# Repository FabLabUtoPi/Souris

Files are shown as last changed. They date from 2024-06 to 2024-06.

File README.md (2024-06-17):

Souris - Projet Souris - Lauréat ANCT  
[Voir le projet sur La Base](https://lesbases.anct.gouv.fr/ressources/souris-adaptee-pour-personne-en-situation-de-handicap-laureat-ami-outiller-la-mediation-numerique)   
# Une souris adaptée pour personnes en situation de handicap
souris_AMI
## A l’origine du projet 
Un ami aveugle de naissance réalise des podcasts. Il se plaint de l’utilisation d’une souris « classique » car parfois lorsqu’il pense déplacer la souris horizontalement pour sélectionner un mot, il la déplace en diagonale et sélectionne plusieurs mots, plusieurs lignes. Il existe des souris adaptée mais leur prix est hors de sa portée car les aides ne couvrent pas la dépense à engager.
Le projet d’une souris adaptée est proposé au FabLab et accepté.
## L’approche du FabLab UtoPi
### Cahier des charges
#### Généralités
Au sein du **FabLab UtoPi** se crée une équipe qui va se consacrer au développement de la souris adaptée. Au vu des prix pratiqués pour ce genre de matériel (~700 à 800€), le premier élément pris en compte est le coût. Il est décidé de limiter le coût de la souris aux alentours de 50€ maxi pour la mettre à la portée d’un maximum de personnes.

#### Choix du microcontrôleur
Au sein du **FabLab UtoPi** plusieurs possibilités de développement existent. Les microcontrôleurs utilisés sont le STM32, la famille des PIC, Arduino et Raspberry Pi PICO. 
En raison des possibilités de programmation en MicroPython du Raspberry Pi PICO, ce qui le rend accessible à un plus large nombre d’utilisateurs (le langage Python est le langage choisi par l’Éducation Nationale pour les lycées), c’est ce modèle qui a été choisi. Son prix autour de 5€ permet de conserver un prix raisonnable pour les souris produites.

#### Déplacement du curseur

Pour limiter les déplacements aux directions HAUT, BAS, DROITE et GAUCHE, le choix s’est porté sur un joystick. Celui-ci permet de plus une adaptation en cas de problème de préhension. Les tests avec un joystick analogique (avec des potentiomètres) et un numérique (avec des switch) ont abouti au choix de la version numérique.
Si l’utilisateur déplace le joystick en diagonale (volontairement ou par inadvertance), il sera averti par un vibreur intégré à la souris, qui fournit un retour haptique.

#### Boutons additionnels
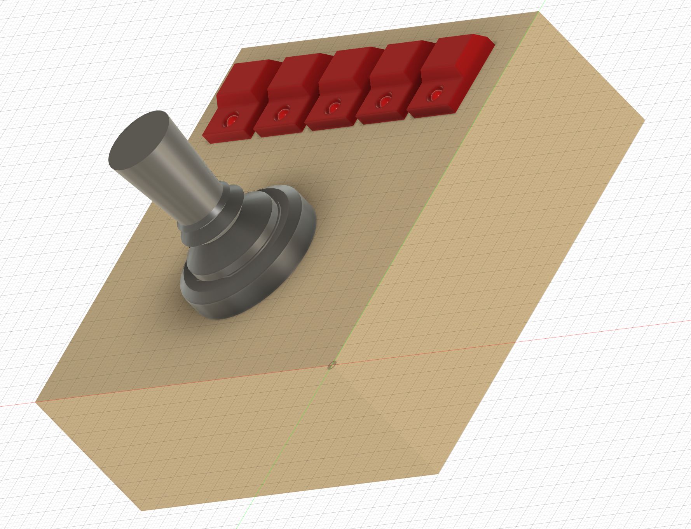
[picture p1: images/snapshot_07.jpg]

Lorsque le joystick sera maintenu en position un certain temps (programmable), le curseur sur l’écran se déplacera automatiquement dans la direction choisie. 
Boutons additionnels
La souris sera dotée de 5 boutons placés devant le joystick. Selon les retours d’expérience, ce nombre pourra être modifié ainsi que les emplacements. Les fonctions retenues pour ces boutons sont : Clic gauche, clic droit, appel d’un logiciel (programmable, par défaut NVDA), roulette UP, roulette DOWN.

#### Le retour haptique
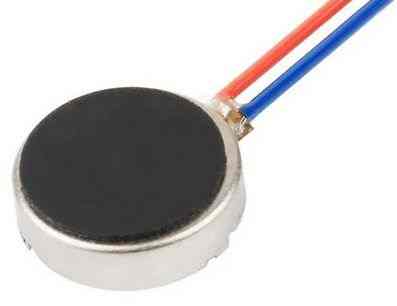
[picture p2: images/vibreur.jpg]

Pour assurer un retour haptique (tactile), la souris sera munie d’un vibreur. C’est un moteur miniature qui entraîne une masselotte excentrée et produit des vibrations. Ce genre de vibreur équipe les tablettes et les smartphones. Le vibreur pourra signaler des actions comme le déplacement en diagonale, confirmer l’activation d’une touche…
Une action lors de la connexion de la souris (appui sur touche ou combinaison de touches) permettra de dévalider l’utilisation du retour haptique.

#### Retour auditif
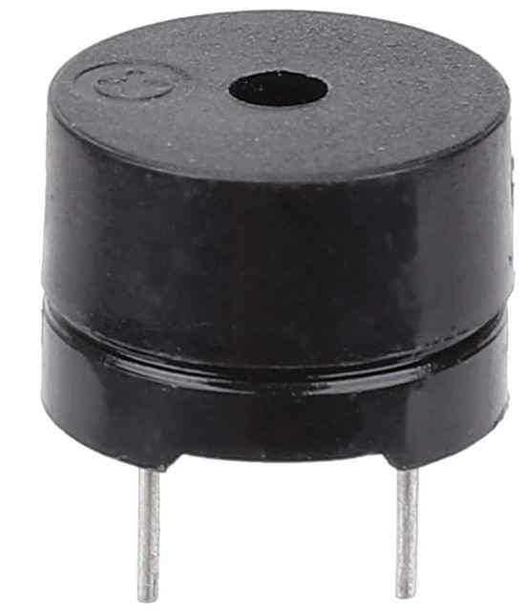
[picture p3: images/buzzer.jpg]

Un retour auditif (sous forme de clic ou de bip) est envisagé avec la présence d’un buzzer activé par une des sorties du Raspberry Pi PICO. 
Une action lors de la connexion de la souris (appui sur touche ou combinaison de touches) permettra de dévalider l’utilisation du retour auditif.  

#### Sortie du programme
La programmation du Raspberry Pi PICO se fait via la connexion USB. Une combinaison touche/joystick sera prévue pour arrêter le programme et donner accès au microcontrôleur pour pouvoir modifier le programme.
Combinaison prévue : Touche centrale + touche la plus à droite + joystick en BAS. Si cette combinaison est activée en cours de programme, le programme allume les LEDs des 5 touches, envoie sur le port console un message d’avertissement, puis s’arrête. Cela permet au développeur de reprendre la main pour apporter plus facilement des modifications. Sur les modèles définitifs cette fonction pourra être dévalidé.  

## Réalisation technique
### Brochage du Raspberry Pi PICO
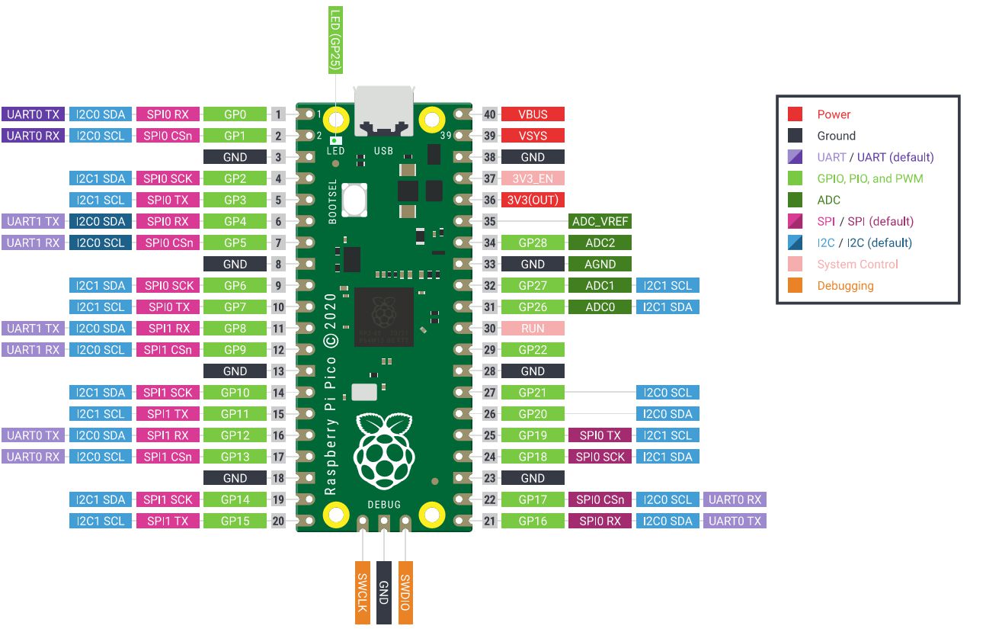
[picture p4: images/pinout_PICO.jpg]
  
Le Raspberry Pi PICO expose ses Entrées/Sorties GPIO comme ci-dessus. Le choix a été fait d’utiliser la partie gauche de la carte pour connecter les différents matériels utilisés (switch, LEDs, vibreur et buzzer). Les bornes de masse (GND) intercalées permettent de connecter la masse aux endroits souhaités.
La partie droite comporte une dizaine de GPIO supplémentaires, dont des possibilités d’Entrée Analogique qui pourront éventuellement être utilisées pour des développements futurs.\\\

### Schéma global de la souris adaptée
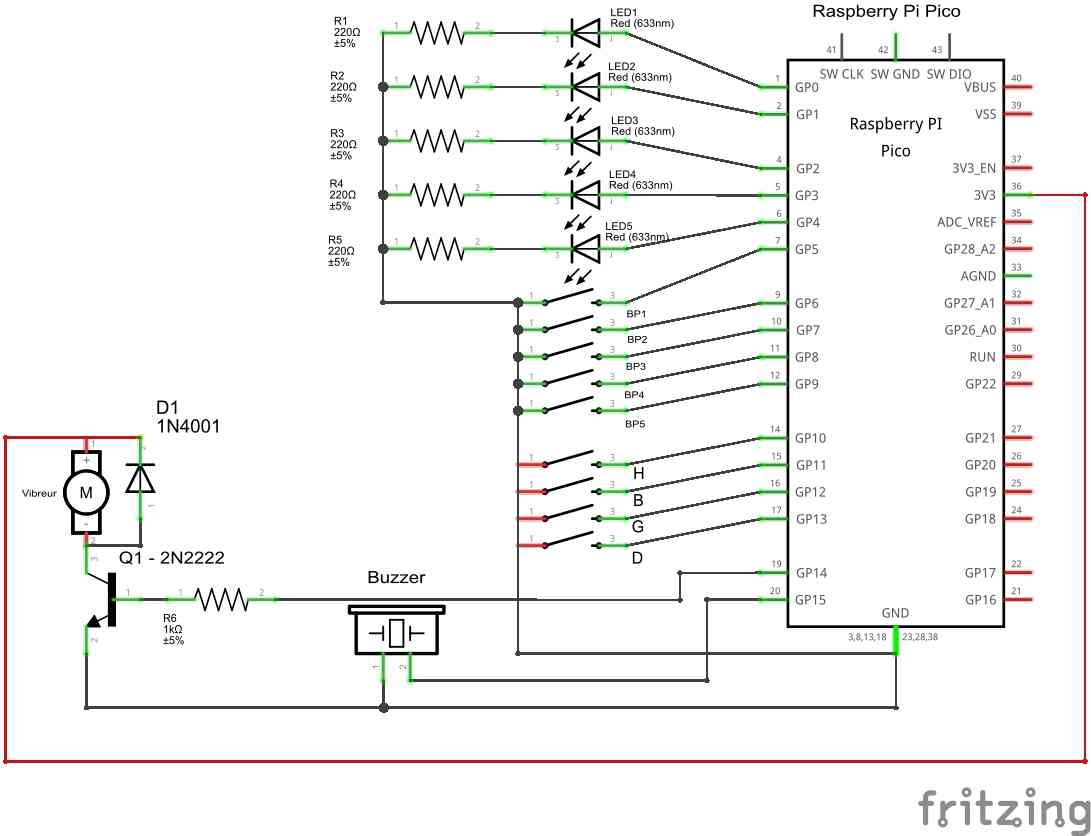
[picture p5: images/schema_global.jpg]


Le schéma montre la connexion des LEDs (GP0 à GP4), des 5 boutons poussoirs (GP5 à GP9) et du joystick (GP10 à GP13). 
Le vibreur est connecté à la sortie GP14, et le buzzer à la sortie GP15.
La sortie GP15 active le vibreur. La diode anti retour aux bornes du moteur est nécessaire avec le moteur utilisé.

### Plaque support des boutons poussoirs
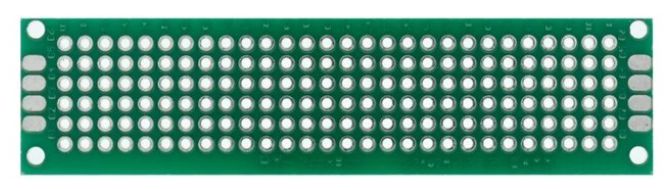
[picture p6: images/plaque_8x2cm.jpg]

La plaque support des boutons poussoirs choisie est un modèle de carte prototype double face universel. Pour la version définitive on pourra envisager la fabrication d’un PCB (circuit imprimé) sur mesure et plus adapté. Mais pour le prototype, cette solution était la plus rapidement mise en œuvre.

### Câblage des Boutons poussoirs
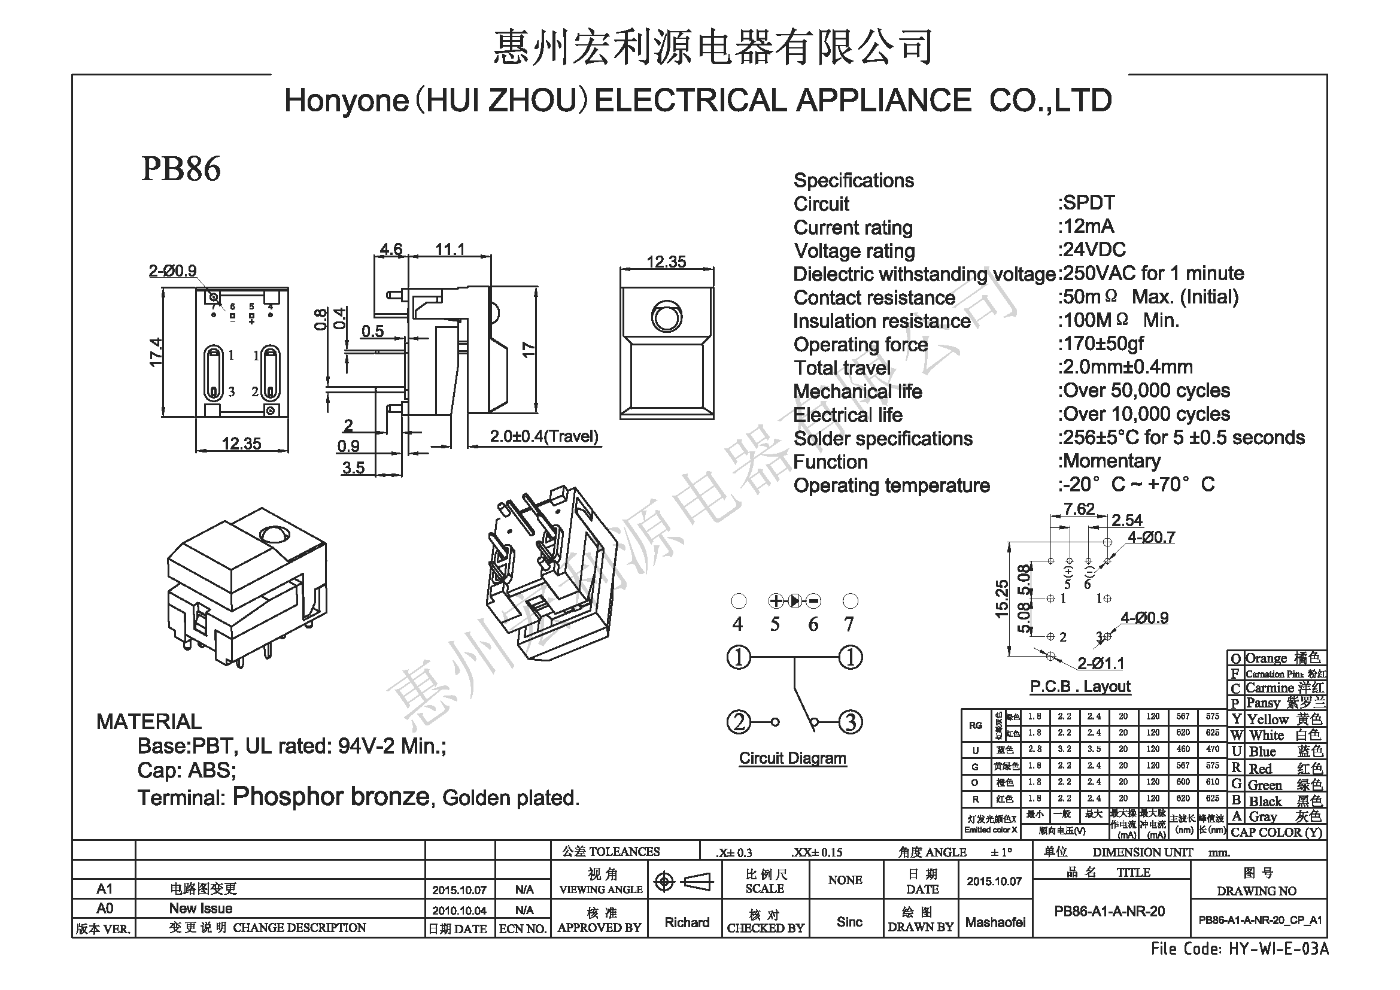
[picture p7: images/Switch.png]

Les boutons poussoirs sont documentés ci-dessus. En position repos, les broches 1 et 3 sont reliées (position NF = Normalement Fermé). Quand on appuie sur le bouton poussoir 1-3 s’ouvre et 1-2 se ferme (NO = Normalement ouvert).
La LED est connectée aux bornes 5 (anode) et 6 (cathode). Il conviendra d’ajouter une résistance en  série avec la LED pour protéger la sortie du Raspberry Pi PICO. Cette résistance vaudra au minimum 220 Ω, une valeur supérieure réduira la luminosité de la LED.
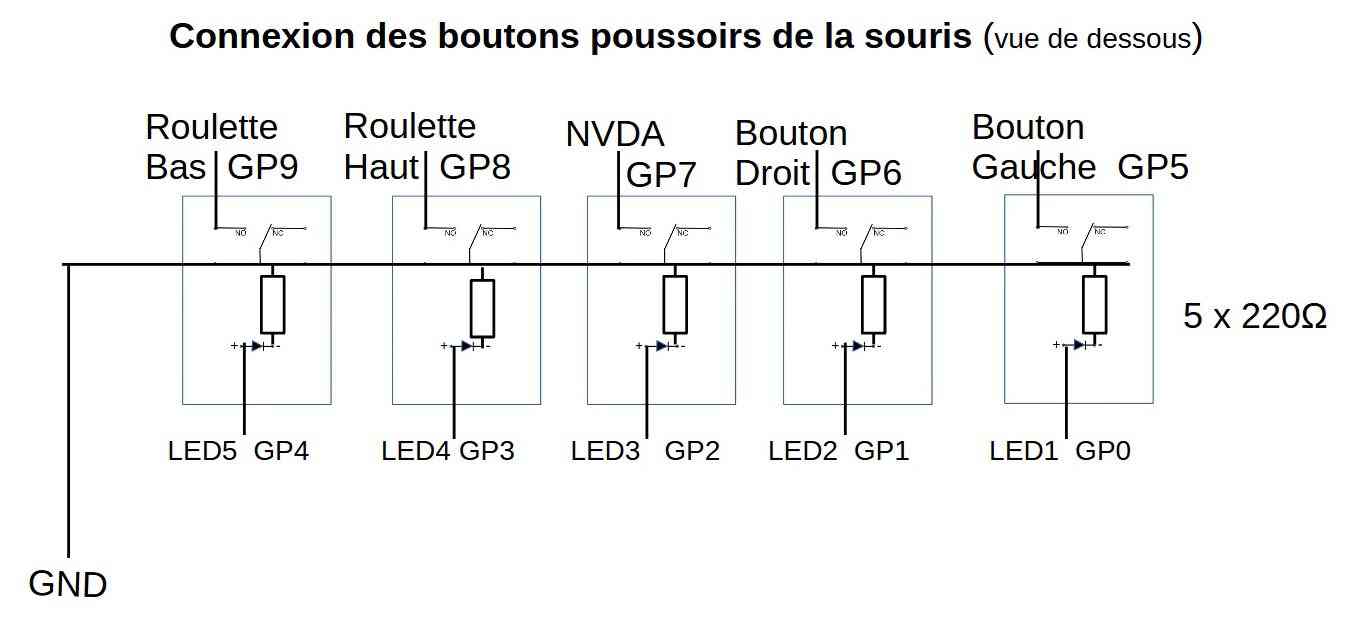
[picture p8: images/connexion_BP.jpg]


Le câblage des boutons poussoirs et des LEDs est ici représenté vu de dessous. Sur la plaque prototype, des fils ont été soudés et relient les différents éléments (voir photo)

### Câblage du joystick
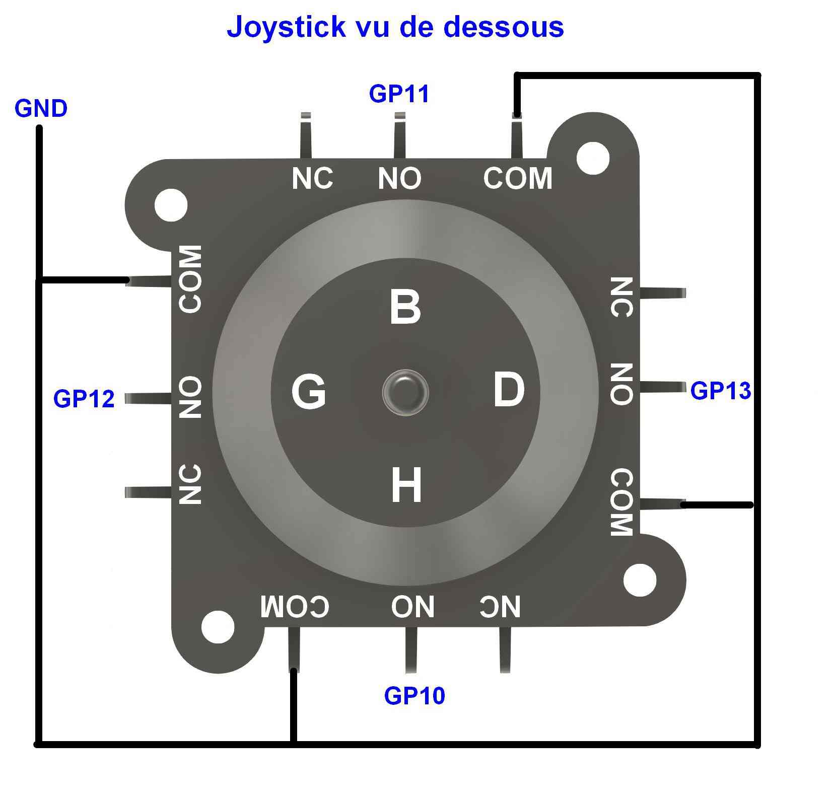
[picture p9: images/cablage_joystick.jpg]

Nota : En fonction de la position de montage du joystick, il faudra éventuellementadapter le programme.  

Le câblage du joystick ne pose pas de problème particulier. Lorsque l’utilisateur pousse le manche du joystick dans une direction, le switch concerné établit un contact entre les bornes COM et NO.  

### Connexion du vibreur au Raspberry Pi PICO
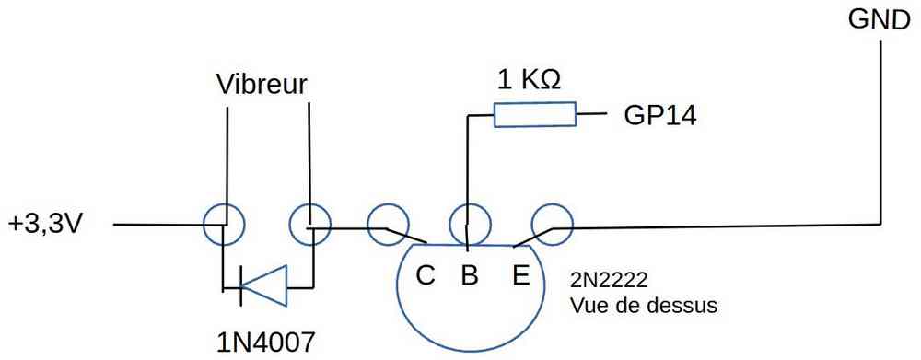
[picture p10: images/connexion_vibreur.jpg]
  
La sortie GP14 du Raspberry Pi PICO ne peut pas fournir le courant nécessaire pour actionner le moteur du vibreur (~ 200 mA max.). Un transistor 2N222 ou équivalent reçoit le signal et commande le vibreur.

# Modélisation 3D du boîtier de la souris
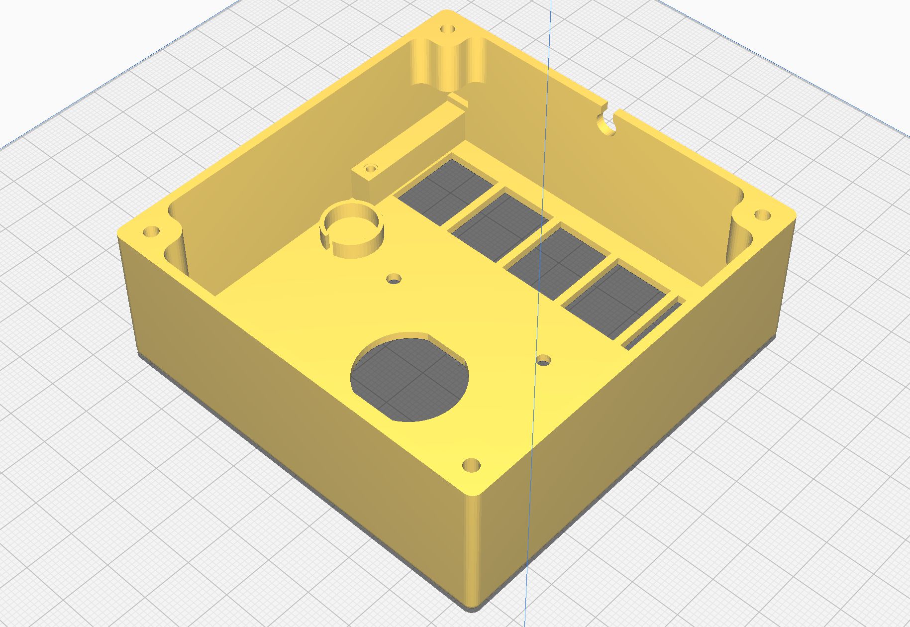
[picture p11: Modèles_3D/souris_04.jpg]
  

La modélisation a été faite avec Fusion 360. Les fichiers sont disponibles dans le dossier Modèles_3D

# Logiciel de Gestion de la souris
## Choix du micrologiciel
Le micro-logiciel installé sur la souris est Circuit Python. Python est le langage de programmation qui connaît la plus forte croissance. Il est enseigné dans les lycées et les universités. C'est un langage de programmation de haut niveau, ce qui signifie qu'il est conçu pour être facile à lire, à écrire et à maintenir. Il prend en charge les modules et les paquets, ce qui signifie qu'il est facile de réutiliser un code existant pour d'autres projets. Il dispose d'un interpréteur intégré, ce qui signifie qu'il n'y a pas d'étapes supplémentaires, comme la compilation, pour faire fonctionner le code qui a été écrit. De plus , Python est un logiciel libre, ce qui signifie que tout le monde peut l'utiliser, le modifier ou l'améliorer
CircuitPython ajoute la prise en charge du matériel à toutes ces caractéristiques du langage Python. Si quelqu’un a déjà des connaissances en Python, il peut facilement les appliquer à l'utilisation de CircuitPython. Si l’utilisateur n'a aucune expérience préalable, il est très simple de commencer avec ce langage ! La version de Circuit Python est adaptée au modèle de carte à programmer. Dans notre cas c’est [la version 8.2.7](https://circuitpython.org/board/raspberry_pi_pico/)  qui était disponible pour le Raspberry Pi PICO au moment de la création du prototype. 
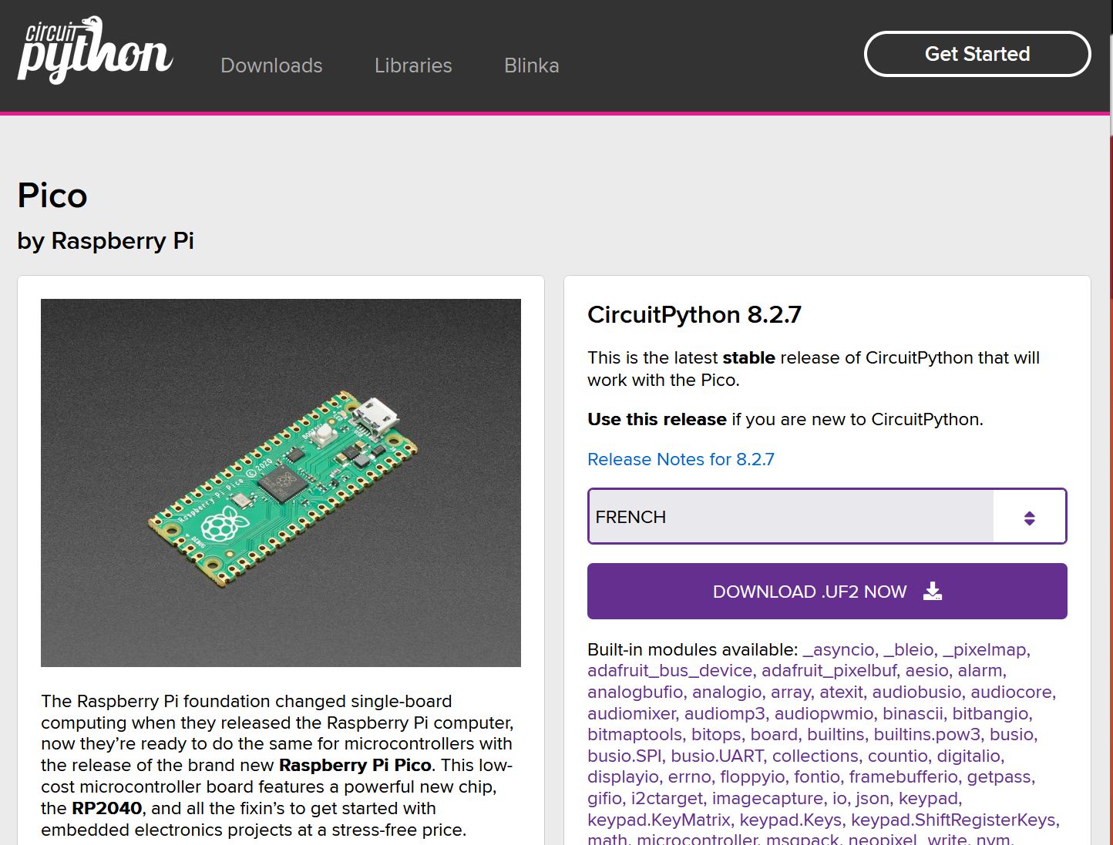
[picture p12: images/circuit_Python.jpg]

(source [circuitpython.org](https://circuitpython.org/))
## Installation de Circuit Python
A partir de la page ci-dessus, sélectionnez la langue (French), et téléchargez le micrologiciel. Il est disponible au format .uf2. 
Commencez avec le Raspberry Pi PICO débranché. Appuyez sur le bouton BOOTSEL du Raspberry Pi PICO et connectez la prise USB . Maintenez le bouton appuyé jusqu’à ce qu’une fenêtre RPI-RP2 s’ouvre sur le bureau. Relâchez le bouton BOOTSEL. On accède maintenant à la mémoire du Raspberry Pi PICO comme si c’était une clé USB.  
**Nota :** _Cette opération n’aboutira pas si vous utilisez un câble de charge seule. Vérifiez bien que vous utilisez un câble de données. Si la fenêtre RPI-RP2 n’apparaît pas après un long moment, vérifiez les points indiqués et recommencez l’opération._\
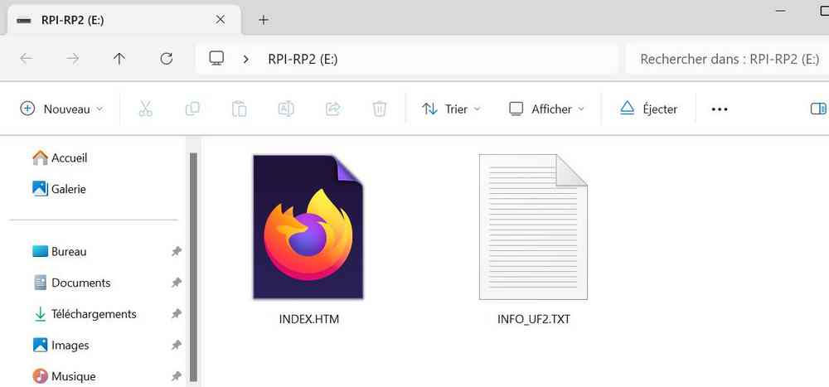
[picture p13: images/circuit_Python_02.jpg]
  

Ouvrez une fenêtre sur le dossier où est enregistré Circuit Python et faites le glisser dans la fenêtre RPI-RP2.  

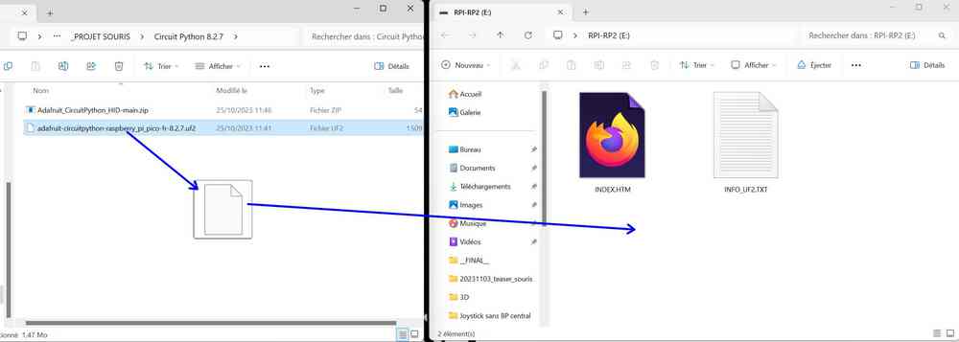
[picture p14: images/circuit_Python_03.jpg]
  
Répondez OK à la demande du système.\

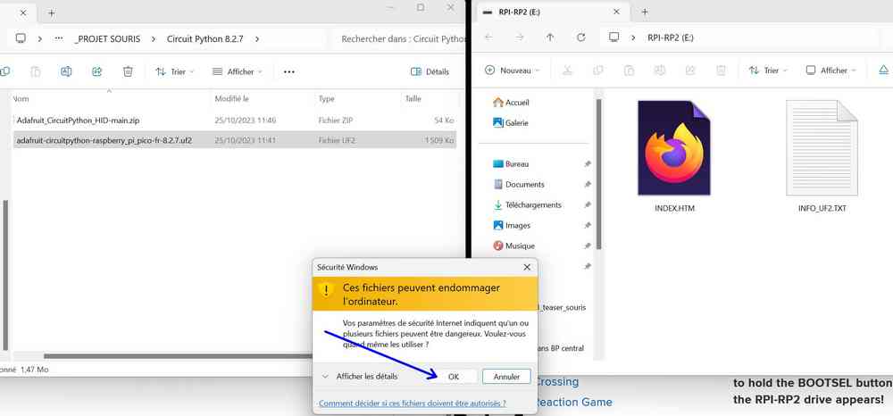
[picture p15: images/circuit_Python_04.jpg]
 

Le fichier est copié dans la mémoire du Raspberry Pi PICO. A la fin du transfert, la fenêtre RPI-RP2 disparaît et le Raspberry Pi PICO redémarre en utilisant circuit Python. La LED interne du Raspberry Pi PICO, située près de la prise USB, clignote une fois toutes les 5 secondes environ.  

**Nota :** _Si votre Raspberry Pi PICO se retrouve dans un état vraiment bizarre et ne s'affiche même pas comme un lecteur de disque lors de l'installation de CircuitPython, essayez d'installer le fichier .uf2 "nuke" qui fera un "nettoyage en profondeur" de votre mémoire flash. Vous perdrez tous les fichiers de la carte, mais au moins vous pourrez reprendre la main ! Après le nettoyage, réinstallez CircuitPython._  

Lien vers le fichier de nettoyage [flash_nuke.uf2](https://cdn-learn.adafruit.com/assets/assets/000/099/419/original/flash_nuke.uf2?1613329170).  

# Installation de Mu
Mu est un éditeur Python simple pour les débutants. C’est l’interface préconisé par Adafruit pour travailler avec Circuit Python.
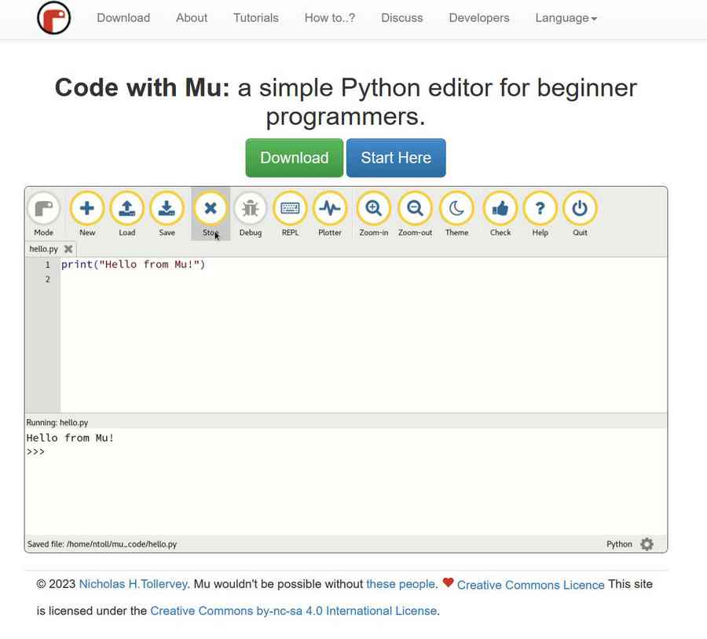
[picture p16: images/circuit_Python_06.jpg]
 
Rendez vous sur [la page de l’éditeur Mu](https://codewith.mu/) et téléchargez (Download) la version correspondant à votre système d’exploitation. Si vous êtes sous Windows, désinstallez les anciennes versions de Mu existant sur votre machine. Installez Mu sur votre machine.
L’installation et le démarrage sont un peu longs, soyez patient.
Au premier démarrage, si la carte Raspberry Pi PICO n’est pas connectée, il faudra choisir le mode de fonctionnement Circuit Python pour Mu.  
Si vous laissez la carte Raspberry Pi PICO, préparée avec Circuit Python, connectée, Mu la détecte et demande si vous voulez passer en mode Circuit Python. Répondez OUI.
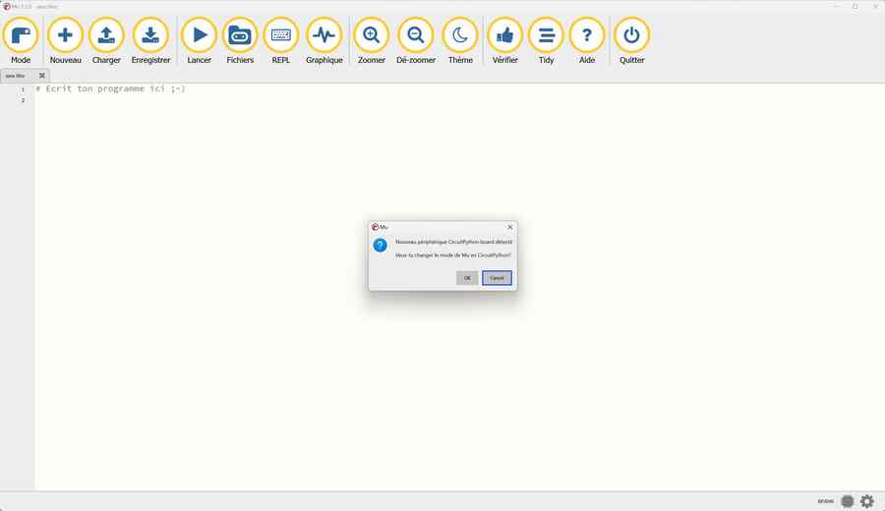
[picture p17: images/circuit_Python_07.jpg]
 
Mu est prêt à être utilisé. On peut le tester avec un Hello World :  

Cliquez sur l’icône Serial, dans la console tapez CTRL + B pour passer en mode REPL. Tapez le code   

print(« Hello World ! »)  

Quand vous tapez sur la touche ENTRÉE la commande est exécutée.  
  

Lorsqu’un programme fonctionne dans un boucle infinie, placez vous dans la fenêtre de la console Circuit Python REPL, puis tapez CTRL + C. Un message vous demande de taper sur une touche quelconque pour reprendre la main :  

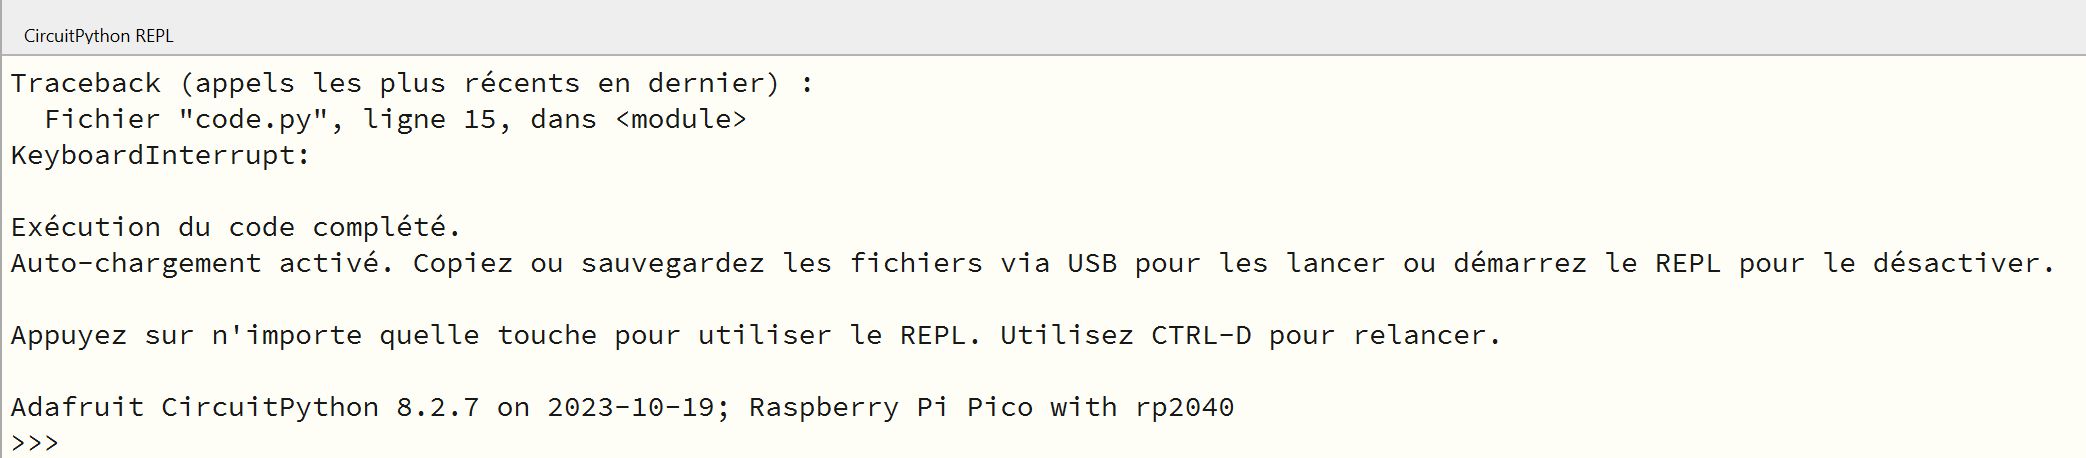
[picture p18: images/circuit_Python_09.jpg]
  

# Cahier des charges logiciel

Le logiciel écrit en Python doit émuler une souris « classique ». Les déplacement privilégiés sont en X et Y, des boutons poussoirs remplacent les boutons Droit et Gauche, ainsi que la roulette. Un bouton programmable permet de déclencher le lancement d’un programme particulier (NVDA, par exemple).
Un retour haptique (vibreur) et sonore (buzzer) permettent de signaler certaine situations à l’utilisateur.  

## Bibliothèque utilisée
La bibliothèque utilisée pour émuler la souris et le clavier est la bibliothèque s’appelle adafruit_hid (HID = Human Interface Device). Téléchargez la bibliothèque sur la page Github [https://github.com/adafruit/Adafruit_CircuitPython_HID](https://github.com/adafruit/Adafruit_CircuitPython_HID), en cliquant sur le bouton vert CODE puis Download ZIP. Dézippez l’archive. Dans le dossier Adafruit_CircuitPython_HID-main créé lors de l’extraction de l’archive, copiez le dossier adafruit_hid qui contient la librairie pour gérer le clavier et la souris. Collez ce dossier dans le dossier lib du Raspberry Pi PICO.  

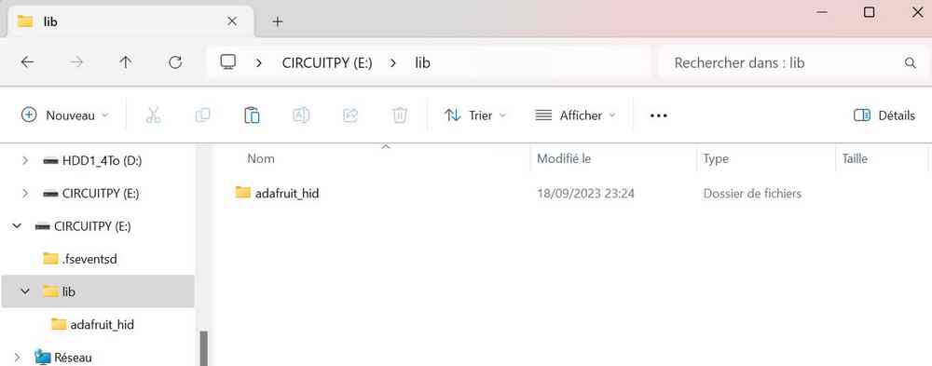
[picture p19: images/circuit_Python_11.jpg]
 

## Description du logiciel souris_v4.py - Rubrique Programmes
Le logiciel de la souris est fourni sous licence open source MIT. 
Les différentes connexions sont définies ainsi :

La position x=0, y=0 pour la souris est en haut à gauche de l'écran
### Connexion des switchs
|   Action    |      |   GPIO  |  
|---    |---    |---    | 
|   UP    |   Souris vers le haut    |   GP12    |  
|   DOWN    |   Souris vers le bas    |    GP13   |       
|   RIGHT    |   Souris vers la gauche    |   GP10    |      
|   LEFT    |    Souris vers la droite   |  GP11     |      
|   |   |   |                              
| GAUCHE  | Appui bouton gauche  | GP5  |                              
| DROITE  | Appui bouton droit  | GP6  |                              
|   |   |   |                              
| PROG  | Lancement programme  | GP7  |                              
|   |   |   |                              
| Wheel UP  | Roulette vers le haut  | GP8  |                              
| Wheel DOWN  | Roulette vers le bas  | GP9  |  

### Connexion des LEDs
|   LED    |  Bouton    |   GPIO  |  
|---    |---    |---    | 
| DROITE  | Bouton droit  | GP0  |                              
| GAUCHE  | Bouton gauche  | GP1  |                              
| PROG  | Lancement programme  | GP2  |                              
| Wheel UP  | Roulette vers le haut  | GP3  |                              
| Wheel DOWN  | Roulette vers le bas  | GP4  |  

| Action  |   | GPIO  |                              
|---   |---   |---   |
| Vibreur  |   | GP14  |                              
| Buzzer  |   | GP15  |                              
                              
A la mise sous tension les LEDs clignotent pour montrer que le programme démarre. Si l'utilisateur ne peut pas voir cette séquence, elle est utile pour la personne qui monte et teste la souris. De même le vibreur est actionné deux fois rapidement.

Si le joystick est manipulé pour bouger la souris en diagonale, une vibration avertit l'utilisateur.
Les touches peuvent être programmées à la demande de l'utilisateur en fonction des logiciels qu'il utilise.
Par défaut elles sont programmées comme suit, de gauche à droite
- Bouton gauche de la souris (clic gauche)
- Bouton droit de la souris (clic droit)
- Ouverture du menu Windows
- Défilement roulette vers le haut
- Défilement roulette vers le bas

# Choix de la licence du logiciel embarqué
Le Logiciel est publié sous licence MIT : _La licence MIT est une licence de logiciel pour logiciels libres1 et open source2, provenant de l'Institut de technologie du Massachusetts (MIT) à la fin des années 1980. Cette licence de logiciel permissive implique très peu de limitations sur la réutilisation du code et elle est ainsi compatible avec de nombreuses autres licences. 
MIT License_ [(source Wikipedia)](https://fr.wikipedia.org/wiki/Licence_MIT)

Copyright (c) 2024 FabLabUtoPi

Permission is hereby granted, free of charge, to any person obtaining a copy
of this software and associated documentation files (the "Software"), to deal
in the Software without restriction, including without limitation the rights
to use, copy, modify, merge, publish, distribute, sublicense, and/or sell
copies of the Software, and to permit persons to whom the Software is
furnished to do so, subject to the following conditions:  

The above copyright notice and this permission notice shall be included in all
copies or substantial portions of the Software.  

THE SOFTWARE IS PROVIDED "AS IS", WITHOUT WARRANTY OF ANY KIND, EXPRESS OR
IMPLIED, INCLUDING BUT NOT LIMITED TO THE WARRANTIES OF MERCHANTABILITY,
FITNESS FOR A PARTICULAR PURPOSE AND NONINFRINGEMENT. IN NO EVENT SHALL THE
AUTHORS OR COPYRIGHT HOLDERS BE LIABLE FOR ANY CLAIM, DAMAGES OR OTHER
LIABILITY, WHETHER IN AN ACTION OF CONTRACT, TORT OR OTHERWISE, ARISING FROM,
OUT OF OR IN CONNECTION WITH THE SOFTWARE OR THE USE OR OTHER DEALINGS IN THE
SOFTWARE.

# Sécurité du logiciel embarqué
Le logiciel n’ayant pas d’interaction avec les logiciels des autres machines, il n’apparait pas de problème de sécurité spécifique

# Liens vers les composants (valable en septembre 2023)
[Carte 8x2 cm pour le câblage des boutons](https://s.click.aliexpress.com/e/_DdNWyrd)  
[Boutons poussoirs avec LED intégrée](https://s.click.aliexpress.com/e/_DdBT0JN)  
[Vibreur pour le retour haptique](https://s.click.aliexpress.com/e/_DFjq7wf)  
[Joystick à 4 axes numériques (switch) sans bouton poussoir central](https://fr.aliexpress.com/item/1005001832652034.html)  
[Joystick à 4 axes numériques (switch) avec bouton poussoir central](https://s.click.aliexpress.com/e/_Dmqzrnh)

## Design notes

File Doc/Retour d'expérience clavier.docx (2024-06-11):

# Retour d’expérience sur le clavier iTunes

## Présentation

La réalisation décrite est un mini clavier de 4 touches pour piloter le logiciel musical iTunes et faciliter l’animation de séances de biodanza au moyen de 4 touches : morceau précédent, play, pause, morceau suivant, en place de manipulation avec la souris. Ce clavier comprend de nombreux points communs avec le clavier pour non-voyant que nous allons développer dans le cadre du projet souris. Ce document décrit les enseignements que j(ai pu en tirer pour la suite.

## Les boutons

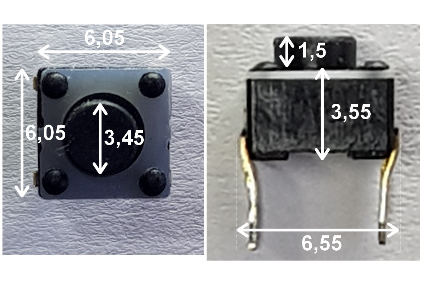
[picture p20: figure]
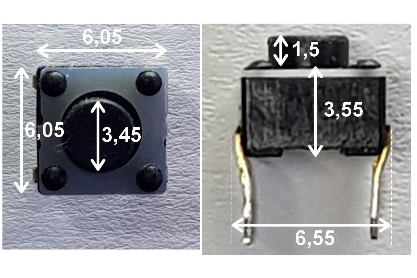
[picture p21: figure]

Le type de bouton retenu est un bouton soudable sur circuit imprimé en traversant au pas de 5,08mm.

Le toucher est agréable avec un contact franc et un clic sonore. Par contre il s’est avéré extrêmement difficile de garder ce rendu au travers de la touche avec un effet ressort. Aucune solution ne m’a donné satisfaction. Le mieux a été un film d’emballage en triple épaisseur (illustration ci-dessous). L’ajustement de l’épaisseur est délicat et il faut aussi jouer sur la profondeur de l’encoche de la touche qui vient dessus.

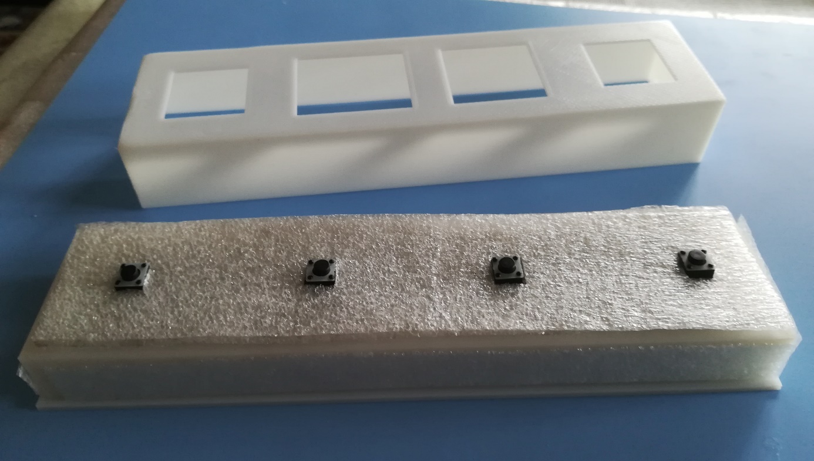
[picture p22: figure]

Pour le clavier destiné à des non-voyants je pense qu’il sera pratique de souder les boutons sur des bouts de plaque type veroboard plutôt que de concevoir un circuit imprimé. Une solution simple à mettre en œuvre reste à trouver pour avoir un effet ressort convenable.

## Les touches

Les touches sont imprimés en 3D. Pour s’adapter au bouton une cavité de 7mm x 7mm et de 3mm de profondeur est creusée sous le bouton.

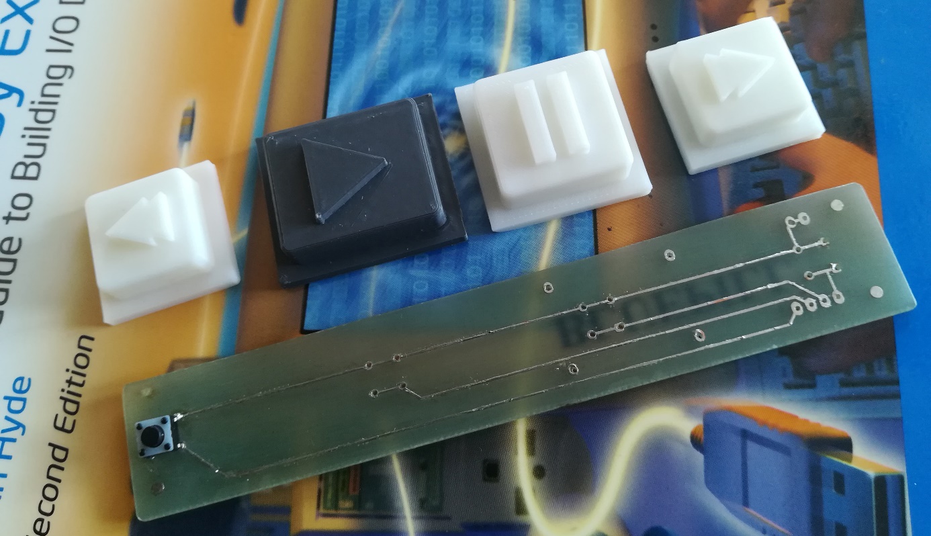
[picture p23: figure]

Faire une touche de grande taille est une fausse bonne idée : il faut appuyer bien au milieu sinon la touche bascule et le contact ne se fait pas. On pourrait imaginer un guidage au prix d’une complexité d’assemblage (utile ?).

Une touche ronde de 18mm de diamètre est conçue sous FreeCAD pour le clavier non-voyant. Voir dans le dossier FreeCAD du dossier partagé « Souris technique », à tester.

## L’interface

Une BluePill STM32 est soudée au dos du circuit imprimé .

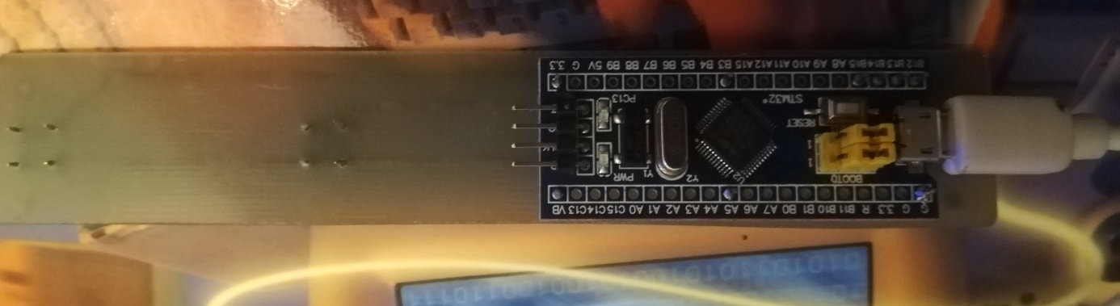
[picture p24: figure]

Le programme permet d’envoyer n’importe quelle touche ou combinaison de touche de clavier standard à partir de l’appui sur un bouton.

Reste à gérer pour le clavier non voyant le codage sur une combinaison de boutons. Un utilitaire permettant de programmer les touches et combinaisons serait un plus.

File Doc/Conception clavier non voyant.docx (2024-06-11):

# Conception d’un clavier adapté pour non-voyant

# (Projet AMI « souris », point début avril 2023)

## Introduction

Des premiers interviews de personnes non-voyantes ressort que ces personnes utilisent quasi exclusivement le clavier via des combinaisons de touches en conjonction avec des logiciels spécifiques disponibles en open source. Partant de ce constat, et sans attendre la rédaction définitive du cahier des charges, on peut imaginer un clavier spécifique adapté aux non-voyants.

Nota : en parallèle se poursuit les interviews des personnes handicapés moteur pour cerner leurs besoins, en particulier en matière d’interface type souris.

## Le clavier

La proposition est un clavier ergonomique avec des touches « tombant » sous les doigts de la main.

Dans l’illustration ci-dessous les boutons sont en couleurs avec un écartement d'une main moyenne, la partie enflée pour poser le creux de la main.

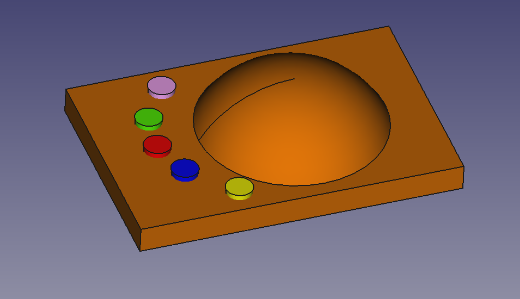
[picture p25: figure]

Chaque touche peut être programmée pour reproduire une combinaison quelconque de touches de clavier pour faciliter l’usage des logiciels spécialisés.

## Les boutons et touches

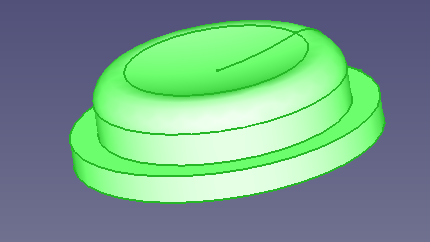
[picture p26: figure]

On utilise un petit bouton au toucher agréable avec un contact franc et un clic sonore, soudable sur un circuit électronique prototype standard. La touche proprement dite recouvre le bouton et est imprimé en 3D. Ci-dessous photo du bouton et modèle 3D de la touche :

## L’interface

Un module électronique programmable et disponible à faible coût permet le codage à volonté des touches et la liaison avec un ordinateur comme clavier standard. Le montage prototype ci-dessous a été réalisé pour valider le concept :

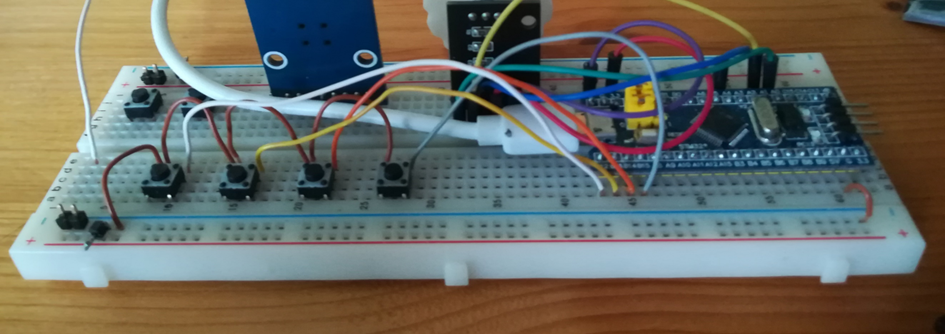
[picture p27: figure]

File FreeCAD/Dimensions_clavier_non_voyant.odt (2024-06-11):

c c

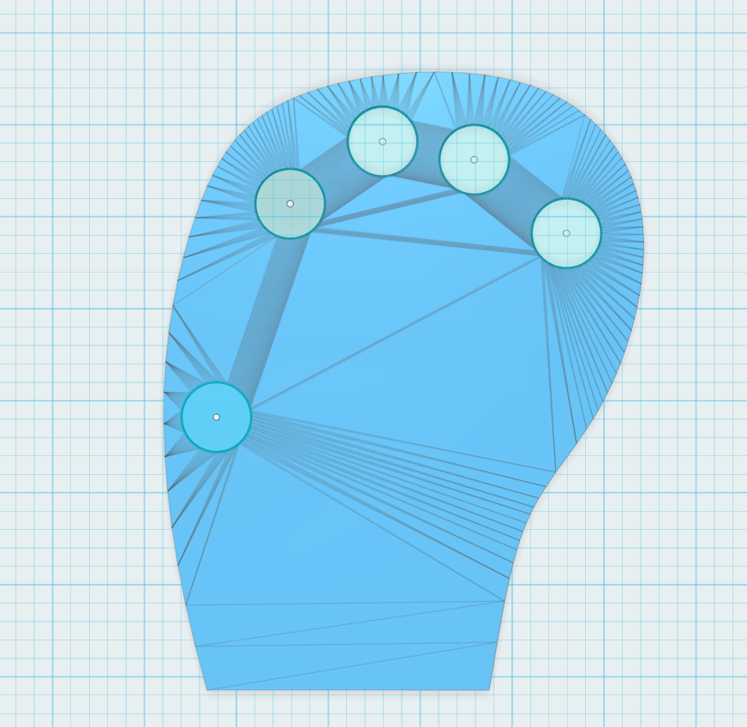
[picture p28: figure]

19,9

58,1

45

75

70

50

70

95

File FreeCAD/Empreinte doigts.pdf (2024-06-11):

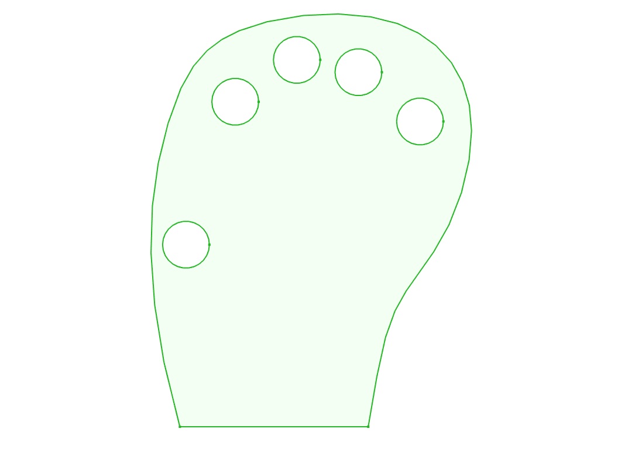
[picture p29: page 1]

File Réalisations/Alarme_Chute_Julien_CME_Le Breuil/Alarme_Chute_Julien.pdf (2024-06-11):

Julien est un pensionnaire du CME du Breuil.
Il est polyhandicapé. Ne parle pas et est en fauteuil roulant.
Il arrive difficilement à se déplacer avec son fauteuil.

Le CME a demandé si il était possible de doter Julien d’un dispositif sonore pour qu’il puisse appeler les encadrants.
Le dispositif doit pouvoir générer 2 signaux sonores distincts selon le degré d’urgence de l’appel :
- 1 signal sonore non urgent (toilette, douche, etc,…..)
- 1 signal sonore pour les situations d’urgences (chute du fauteuil roulant, …..)

Le dispositif proposé se compose d’un boîtier , situé dans la salle commune branché sur une prise murale.

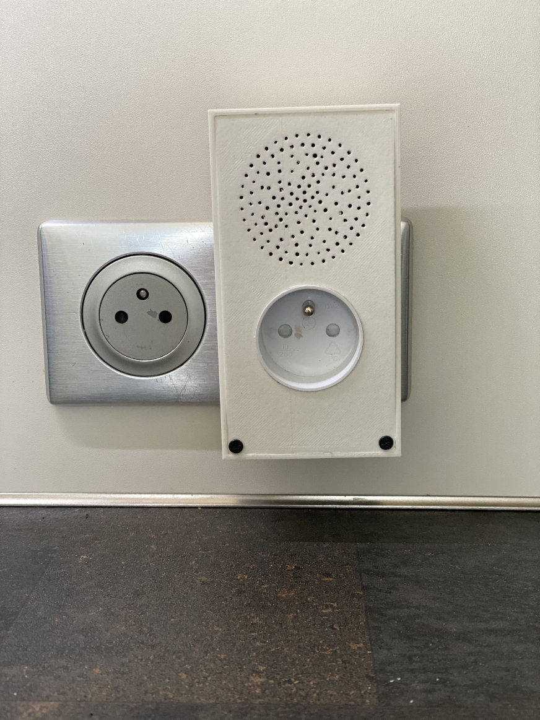
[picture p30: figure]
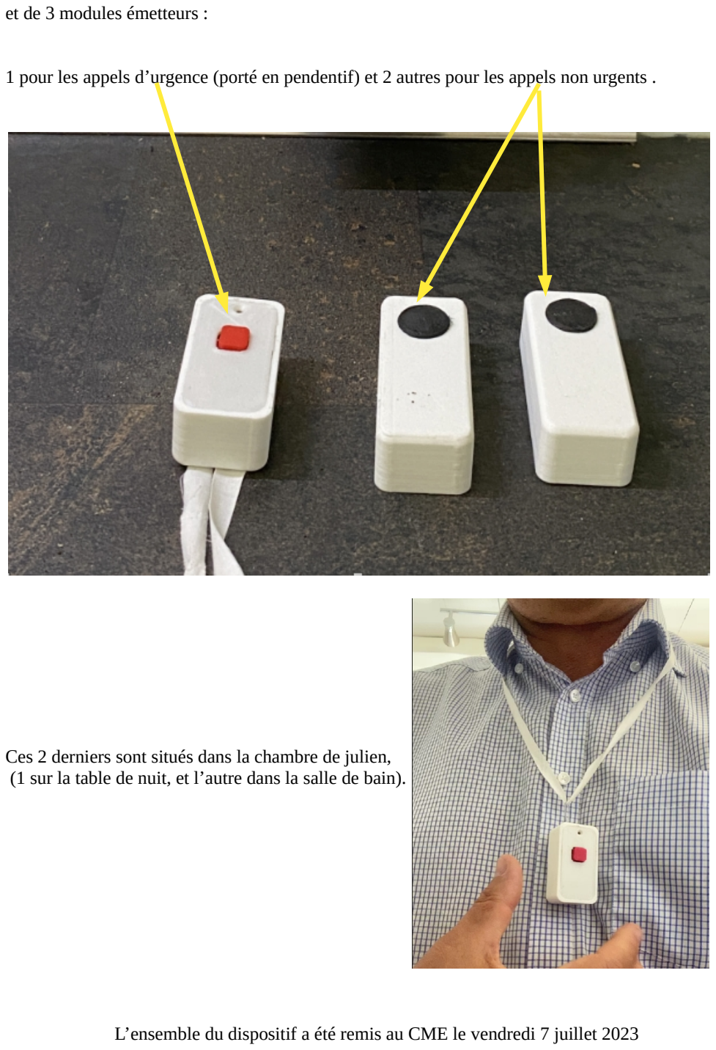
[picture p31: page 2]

et de 3 modules émetteurs :

1 pour les appels d’urgence (porté en pendentif) et 2 autres pour les appels non urgents .

Ces 2 derniers sont situés dans la chambre de julien, (1 sur la table de nuit, et l’autre dans la salle de bain).

L’ensemble du dispositif a été remis au CME le vendredi 7 juillet 2023

ASPECTS TECHNIQUES

Le boîtier mural comporte un récepteur, 433 MHz ; un générateur de séquences sonores réalisé à l »aide d’un micro-controlleur, 1 alimentation 220 V.

Il permet d’utiliser la prise secteur 220V pour un autre appareil (système gigogne)

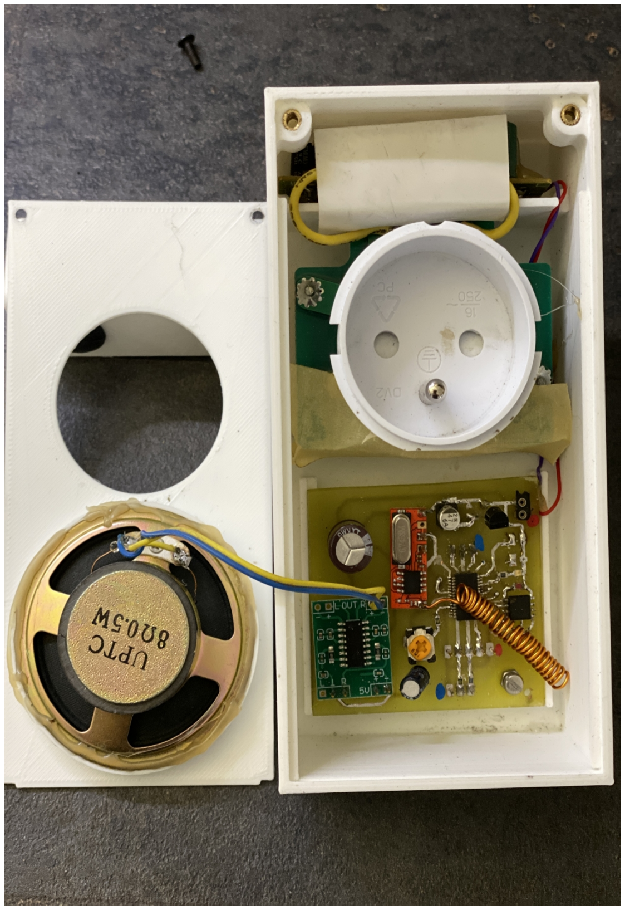
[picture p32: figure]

Tous les fichiers de conception réalisation sont disponibles dans les archives suivantes :

Schéma de principe et tracé du circuit imprimé (A l’aide du logiciel KICAD – V5 ):
Alarme chute_RX_KICAD.rar

Logiciel de programmation du microcontrolleur (PIC16J26K80) – A l’aide du logiciel MPLABX de Microchip.
Alarme_CHUTE_RX_MPLABX.rar

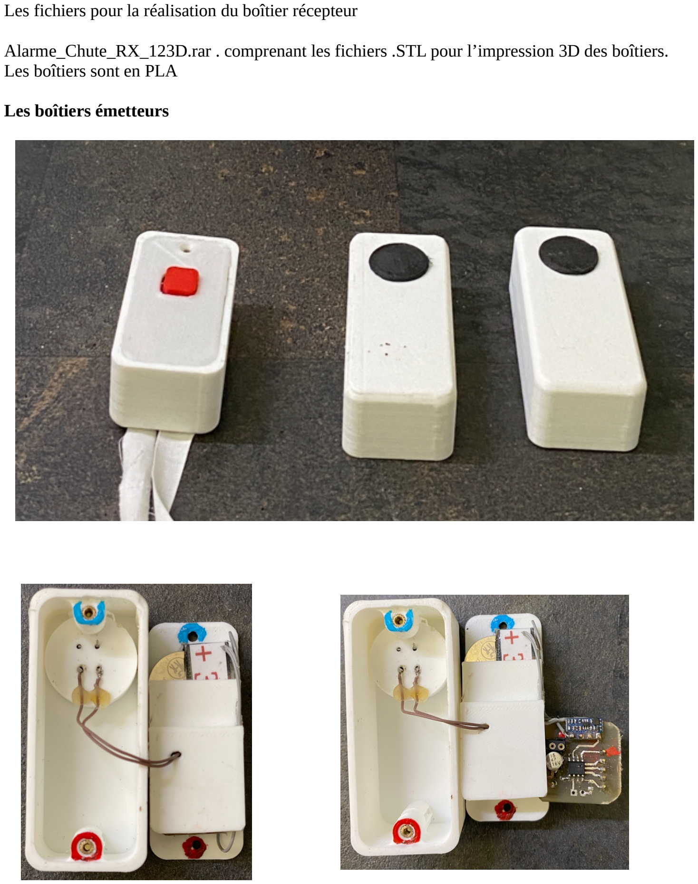
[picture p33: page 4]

Les fichiers pour la réalisation du boîtier récepteur

Alarme_Chute_RX_123D.rar . comprenant les fichiers .STL pour l’impression 3D des boîtiers. Les boîtiers sont en PLA

Les boîtiers émetteurs

Les fichiers de associés :

Alarme chute_TX_KICAD.rar : schéma unifilaire et réalisation circuits imprimés

Alarme_CHUTE_TX_MPLABX.rar : programmation du mico-controlleur (PIC 12F1572)

Alarme_Chute_TX_123D.rar : réalisation en impression 3D des boîtiers avec les bouton. Les boîtiers sont en PLA
Les boutons en PETG dureté Shore D 85.

Une vidéo présente le dispositif.

L’ensemble des document a été déposé dans le référentiel technique.

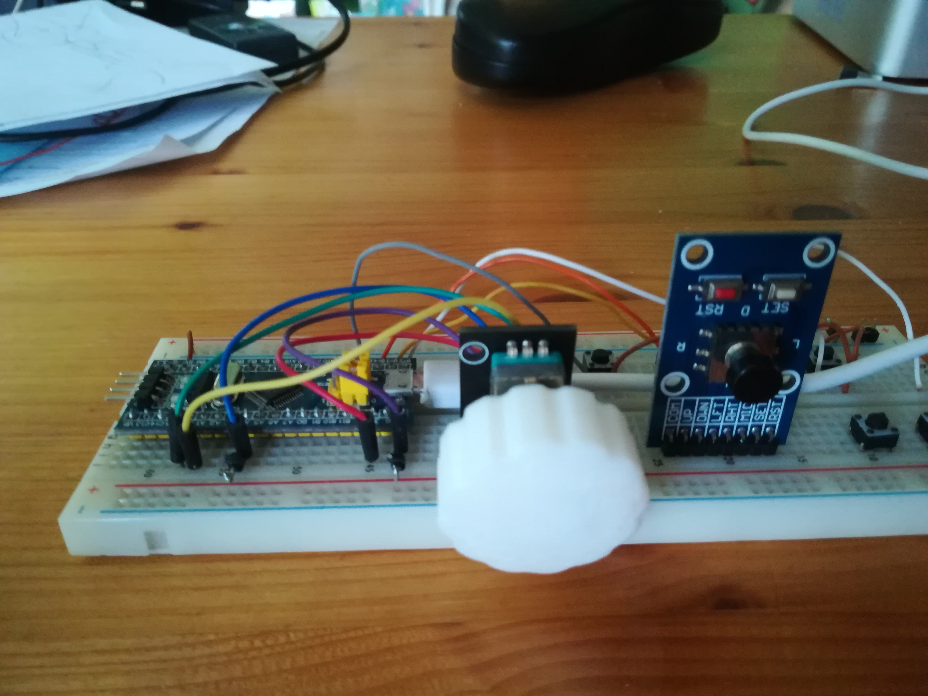
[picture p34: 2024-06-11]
Doc/Illustrations/proto STM32 souris.jpg

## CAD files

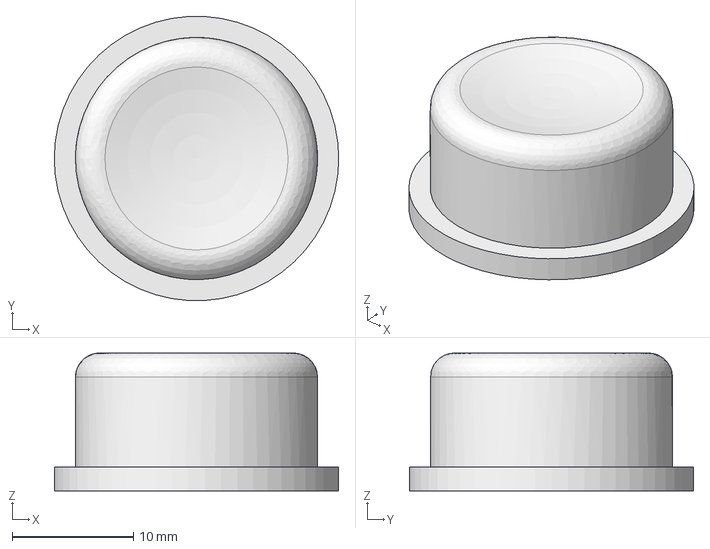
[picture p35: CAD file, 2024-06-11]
FreeCAD/ClavierBoutonRond.FCStd
23.5 x 23.5 x 11.4 mm

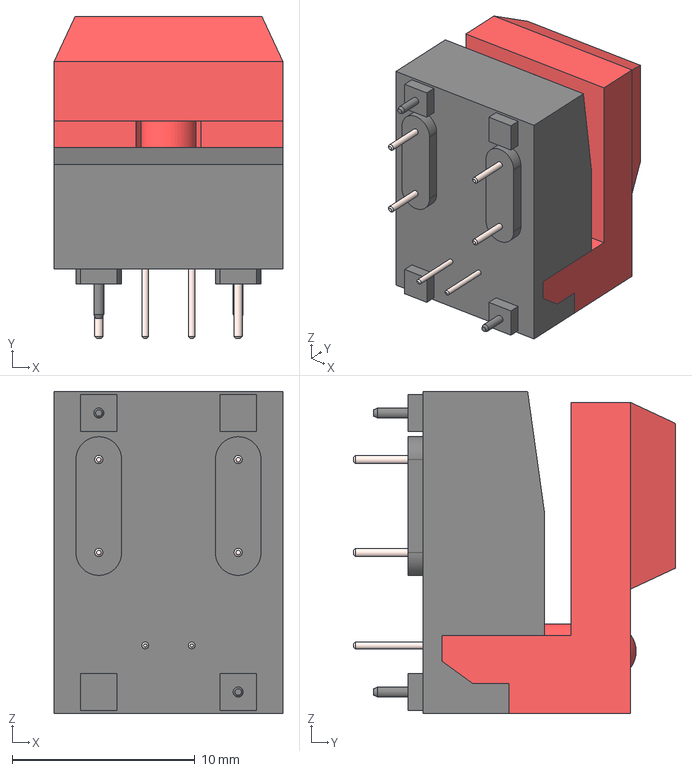
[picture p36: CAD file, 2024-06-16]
Modèles_3D/Switronic MP86A1R1H-G.step
12.5 x 17.6 x 17.6 mm

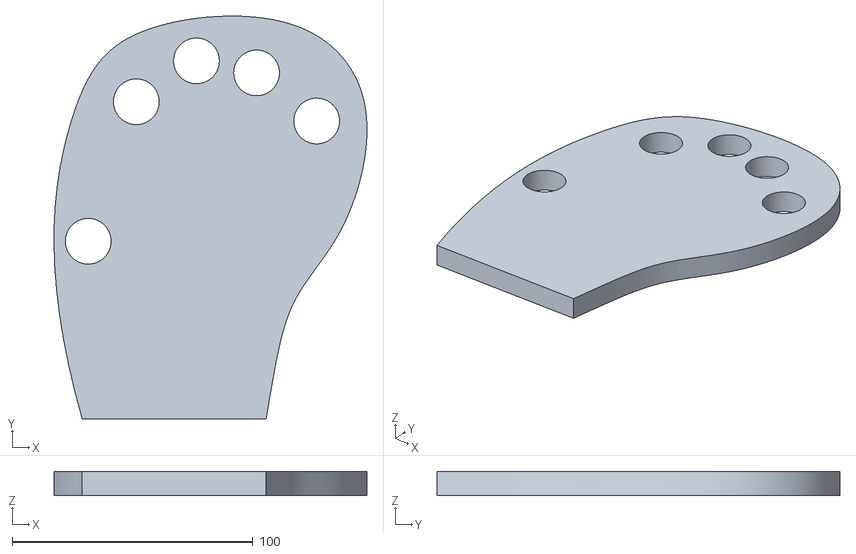
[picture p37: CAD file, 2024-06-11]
FreeCAD/ClavierEmpreinteNonVoyant.stl
130.1 x 167.5 x 10.0

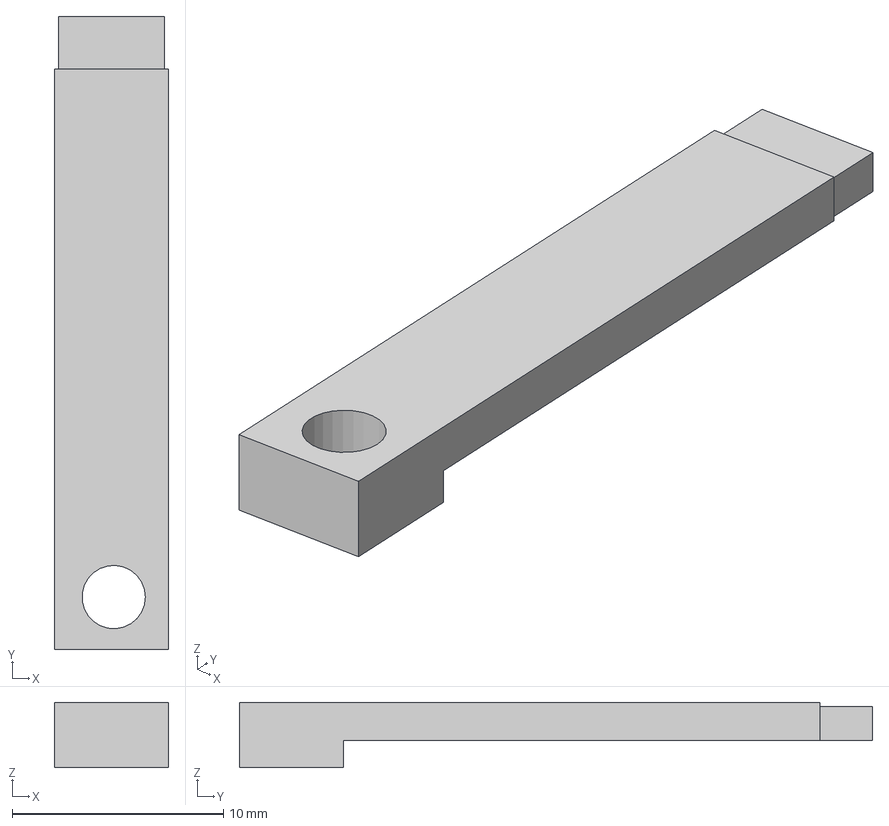
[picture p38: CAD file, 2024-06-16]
Modèles_3D/Clip_fixation v1.3mf
5.40 x 30.0 x 3.10 mm

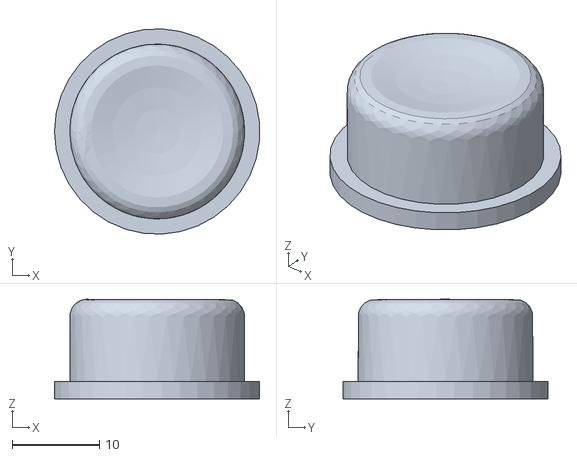
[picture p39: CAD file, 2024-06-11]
FreeCAD/Bouton rond clavier non-voyant.stl
23.5 x 23.5 x 11.4

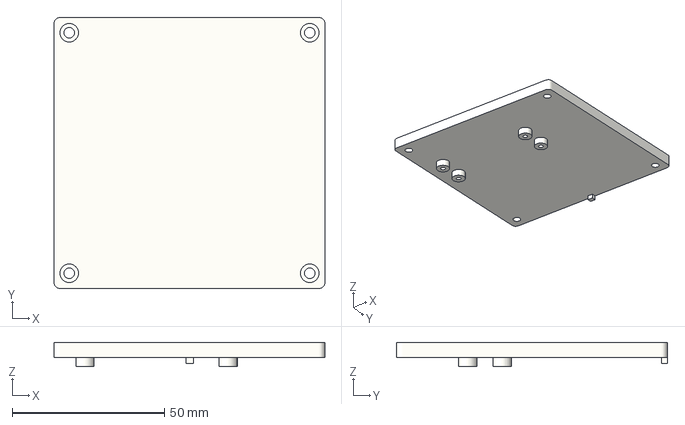
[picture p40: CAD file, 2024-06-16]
Modèles_3D/Boite_partie_basse v3.3mf
89.0 x 89.0 x 8.00 mm

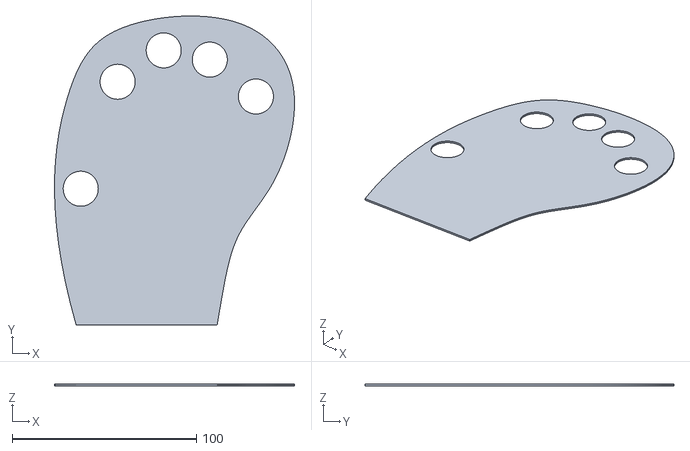
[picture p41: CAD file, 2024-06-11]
FreeCAD/ClavierEmpreinteNonVoyant1mm.stl
130.1 x 167.5 x 1.00

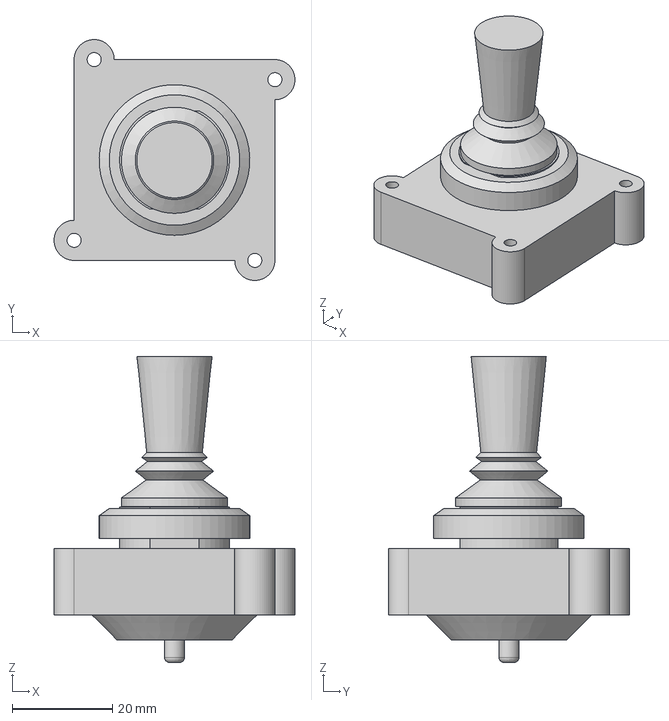
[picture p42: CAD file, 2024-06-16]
Modèles_3D/joystick monolever CV4-YQ-04R2G.step
48.0 x 48.0 x 61.0 mm

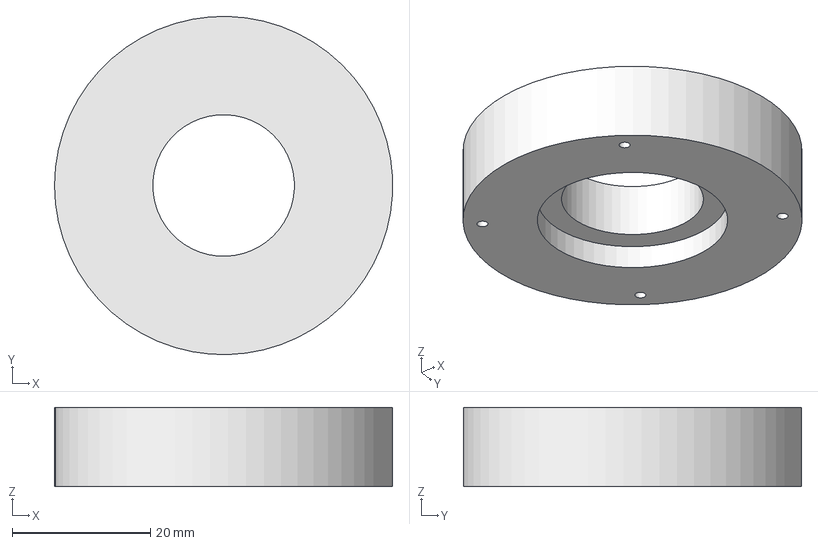
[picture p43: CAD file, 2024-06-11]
FreeCAD/TestCapsuleBouton.FCStd
48.9 x 49.0 x 11.5 mm

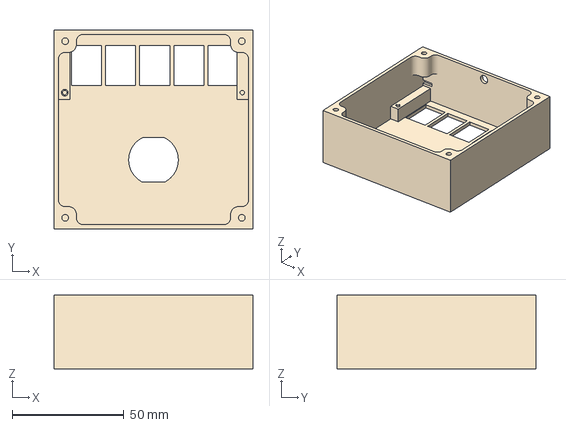
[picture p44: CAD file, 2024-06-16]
Modèles_3D/Boite_partie_haute_v4_20231018.3mf
89.0 x 89.0 x 33.0 mm

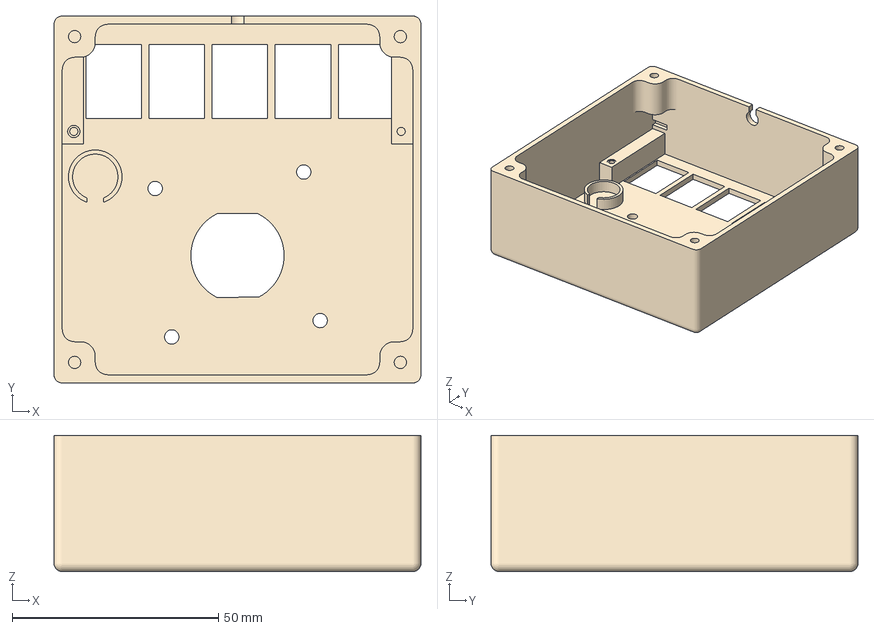
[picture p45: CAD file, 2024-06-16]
Modèles_3D/Souris ANCT v1.3mf
89.0 x 89.0 x 33.0 mm

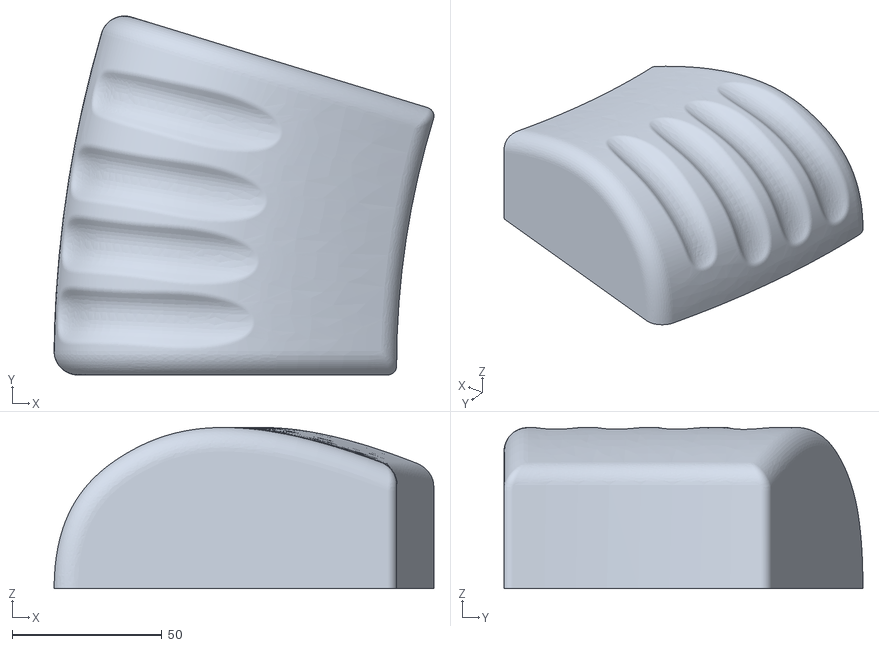
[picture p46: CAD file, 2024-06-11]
FreeCAD/SourisUtopiCoque.stl
126.7 x 119.7 x 53.7

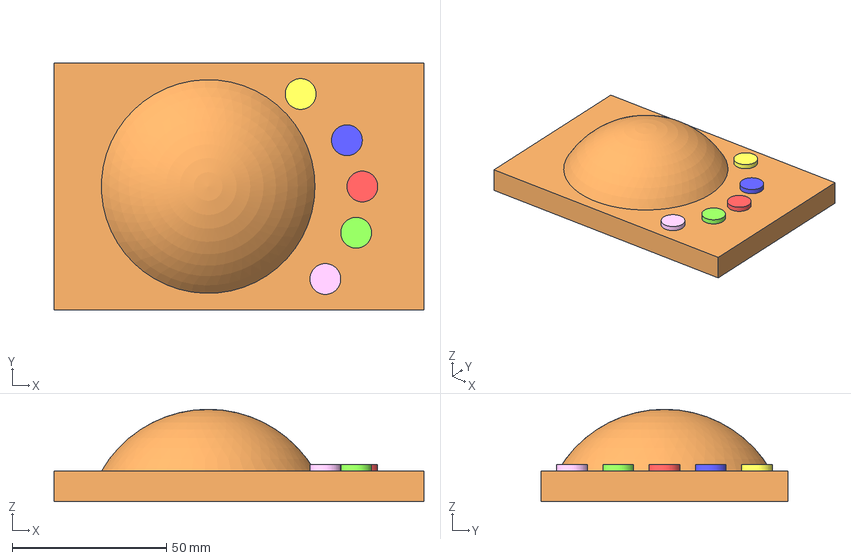
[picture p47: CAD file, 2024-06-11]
FreeCAD/Ebauche clavier non voyant.FCStd
120.0 x 80.0 x 30.0 mm
socle
repose main
Touche majeur
Touche index
Toche pouce
Touche annulire
Touche auriculaire

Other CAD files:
FreeCAD/ClavierEmpreinteBoutons.FCStd
FreeCAD/SourisUtopi.FCStd
FreeCAD/TestCapsuleBouton.stl
Modèles_3D/Clip_fixation v1.stl
Modèles_3D/joystick monolever CV4-YQ-04R2G.stl

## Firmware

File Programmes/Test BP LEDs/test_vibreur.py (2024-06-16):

# Importer la librairie machine - Pin
from machine import Pin, PWM
# Importer Sleep
from time import sleep
import sys

# Définir le Buzzer
buzzerPIN=15
BuzzerObj=PWM(Pin(buzzerPIN))

# Fonction du Buzzer
def buzzer(buzzerPinObject,frequency,sound_duration,silence_duration):
    # Set duty cycle to a positive value to emit sound from buzzer
    buzzerPinObject.duty_u16(int(65536*0.2))
    # Set frequency
    buzzerPinObject.freq(frequency)
    # wait for sound duration
    sleep(sound_duration)
    # Set duty cycle to zero to stop sound
    buzzerPinObject.duty_u16(int(65536*0))
    # Wait for sound interrumption, if needed 
    sleep(silence_duration)


# Déclarer les LEDs des Boutons Poussoirs
pin_led1 = Pin(0, mode=Pin.OUT, value=1)
pin_led2 = Pin(1, mode=Pin.OUT, value=1)
pin_led3 = Pin(2, mode=Pin.OUT, value=1)
pin_led4 = Pin(3, mode=Pin.OUT, value=1)
pin_led5 = Pin(4, mode=Pin.OUT, value=1)

# Déclarer les boutons poussoirs
pin_button1 = Pin(5, mode=Pin.IN, pull=Pin.PULL_UP)
pin_button2 = Pin(6, mode=Pin.IN, pull=Pin.PULL_UP)
pin_button3 = Pin(7, mode=Pin.IN, pull=Pin.PULL_UP)
pin_button4 = Pin(8, mode=Pin.IN, pull=Pin.PULL_UP)
pin_button5 = Pin(9, mode=Pin.IN, pull=Pin.PULL_UP)

# Déclarer lejoystick
pin_joystick_H = Pin(10, mode=Pin.IN, pull=Pin.PULL_UP)
pin_joystick_B = Pin(11, mode=Pin.IN, pull=Pin.PULL_UP)
pin_joystick_G = Pin(12, mode=Pin.IN, pull=Pin.PULL_UP)
pin_joystick_D = Pin(13, mode=Pin.IN, pull=Pin.PULL_UP)

# Déclarer le vibreur
buzzerPIN=15
BuzzerObj=PWM(Pin(buzzerPIN))

# Eteindre les LEDs 
def LED_OFF():
    pin_led1.off()
    pin_led2.off()
    pin_led3.off()
    pin_led4.off()
    pin_led5.off()
    
# Allumer les LEDs 
def LED_ON():
    pin_led1.on()
    pin_led2.on()
    pin_led3.on()
    pin_led4.on()
    pin_led5.on()
    
# Attendre 0.2 secondes et éteindre les LEDs
sleep(0.2)
LED_OFF()
sleep(0.2)
LED_ON()
sleep(0.2)
LED_OFF()

# Allumer la LED si un bouton est appuyé
# On sort si les deux boutons extrèmes sont ppuyés
while True:
    if (pin_button1.value() == 1 & pin_button5.value() == 1):
        print("Arrêt du programme")
        LED_OFF()
        buzzer(BuzzerObj,2000,0.05,0.1)
        #Deactivates the buzzer
        BuzzerObj.deinit()
        sys.exit()

    # Gestion de GPIO14
#    pin_vibreur.on()
#    sleep(2)
#    pin_vibreur.off()
#    sleep(2)
#speaker.play(2000, 10) # Play the frequency 523 for 1 second
#sleep(1)
